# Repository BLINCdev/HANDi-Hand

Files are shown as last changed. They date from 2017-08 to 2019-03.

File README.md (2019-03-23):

__HITEC HS 35-HD DISCONTINUATION NOTICE:__ The Hitec servos used in this design have unfortunately been discontinued. We are currently testing other servo options. If you have built or would like to build a HANDi Hand, and would like information about pre-release parts for the new servo change design, please reach out to us at blincdev@gmail.com.

# HANDi Hand
The Humanoid, Anthropometric, Naturally Dexterous, Intelligent (HANDi) Hand is an anthropometric robotic hand designed specifically for machine learning research in prosthetic applications. The HANDi Hand includes 6 degrees of freedom (each finger flexes independently; thumb rotation is separate from thumb flexion). The hand was designed to be 1:1 scale with anatomical proportions and uses Hitec HS-35HD servo-motors. The HANDi Hand is ideally suited for machine learning and sensory feedback research, but can also be used in general purpose robotics applications.

## Build your own HANDi Hand
The HANDi Hand consists of off-the-shelf servomotors, potentiometers, FSRs, metric fasteners, and custom 3D printed parts. Instructions for building the hand and setting up the servos can be found in _'HANDi Hand - Assembly Manual.pdf'_. The assembly manual will be your main go-to document while printing and building the arm and includes references to the other files in the repository:

* __3D Print Files:__ The folder that contains the raw STL files as well as the .THING and .x3g files for 3D printing on a Makerbot Replicator 2. NOTE: The STL files have been adjusted to print with proper tolerances in the PLA material. Further, the print orientation is important for many of the files; refer to the .thing files provided if printing .STL files with other softwares besides MakerWare to ensure the proper print orientation.
* __STEP Files:__ This folder contains the STEP files for each of the parts used in the hand, which should be importable into most 3D CAD softwares.
* __Software:__ This folder contains Arduino sketches that are used for testing the hand during assembly, as well as control of the hand once assembly is complete.

The assembly manual also includes a Bill of Materials: a detailed list of the off-the-shelf materials and parts required to build the HANDi Hand. Note: We have listed the distributors that we have used in the past as a point of reference, but be aware that there are multiple distributor options for each part and that we do not endorse the listed distributors in any way.

## Contributing
You can share your experience, new design, ideas, feature requests, or questions on the [HANDi Hand project forum](https://blincdev.ca/forum/).

If you would like to contribute to future official releases of the HANDi Hand hardware we recommend contacting us on the forums to coordinate with our development team. To get started you will need to [fork this repo](https://help.github.com/articles/using-pull-requests/) and once your modification or enhancement is complete submit a [pull request](https://help.github.com/articles/using-pull-requests/).

## License
The HANDi Hand hardware is released under the [Creative Commons BY-SA 4.0](http://creativecommons.org/licenses/by-sa/4.0/) license. A local copy of the license that was forked from [https://github.com/idleberg/Creative-Commons-4.0-Markdown](https://github.com/idleberg/Creative-Commons-4.0-Markdown) is available in the repository. The HANDi Hand software is released under the [GNU General Public License v3](https://www.gnu.org/licenses/gpl.html). A local copy is available in the repository.

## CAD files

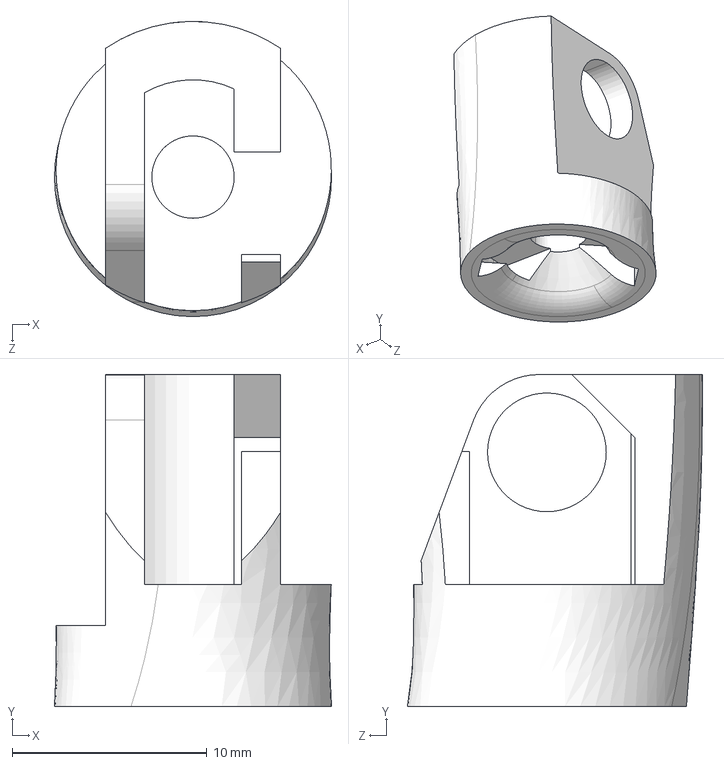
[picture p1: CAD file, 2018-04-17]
Hardware/Left Hand/STEP Files/DP - P Main L.STEP
14.2 x 17.1 x 15.2 mm

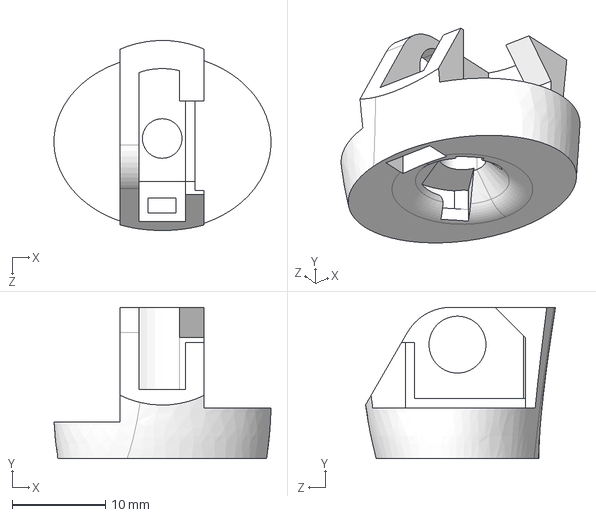
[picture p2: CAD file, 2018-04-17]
Hardware/Right Hand/STEP Files/DP - P MainTH R.STEP
23.2 x 16.2 x 20.4 mm

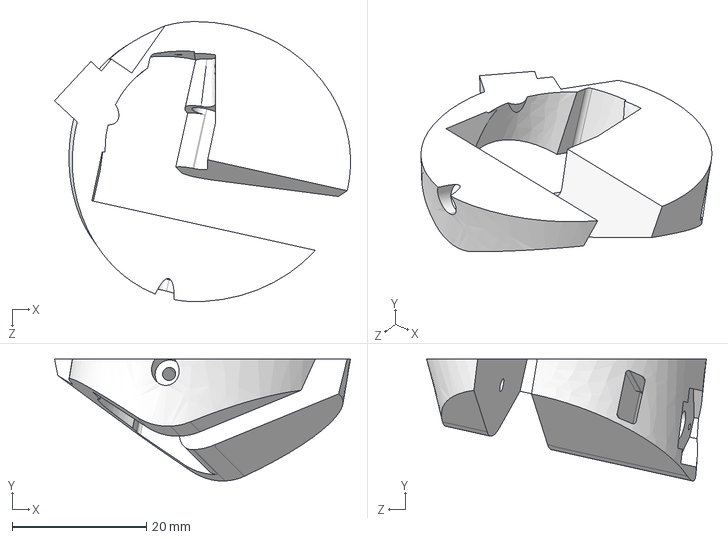
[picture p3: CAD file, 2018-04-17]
Hardware/Right Hand/STEP Files/MC - P Main R - Add B.STEP
44.2 x 18.2 x 41.8 mm

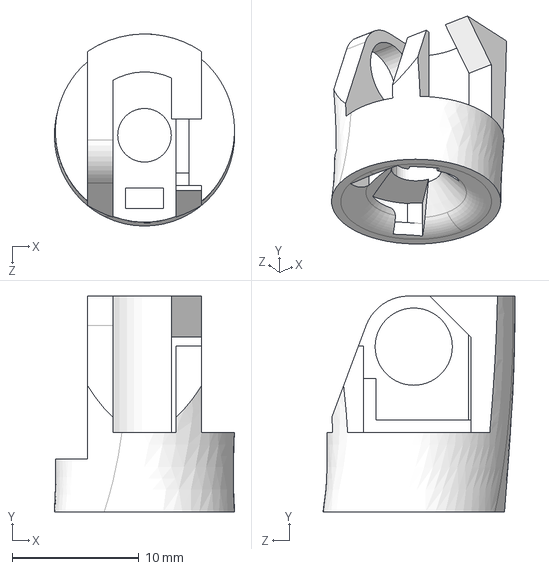
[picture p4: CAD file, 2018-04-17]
Hardware/Right Hand/STEP Files/DP - P Main R.STEP
14.2 x 17.1 x 15.2 mm

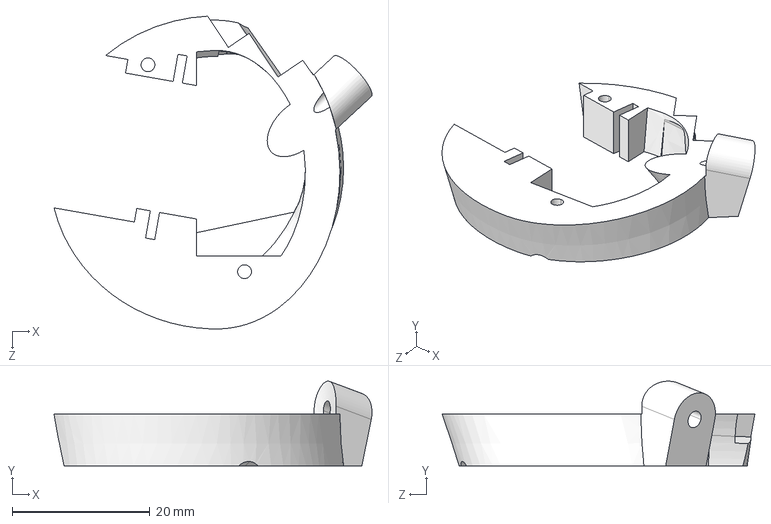
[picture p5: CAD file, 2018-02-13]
Hardware/Left Hand/STEP Files/MC - P Main L - Add A.step
46.1 x 12.3 x 45.3 mm

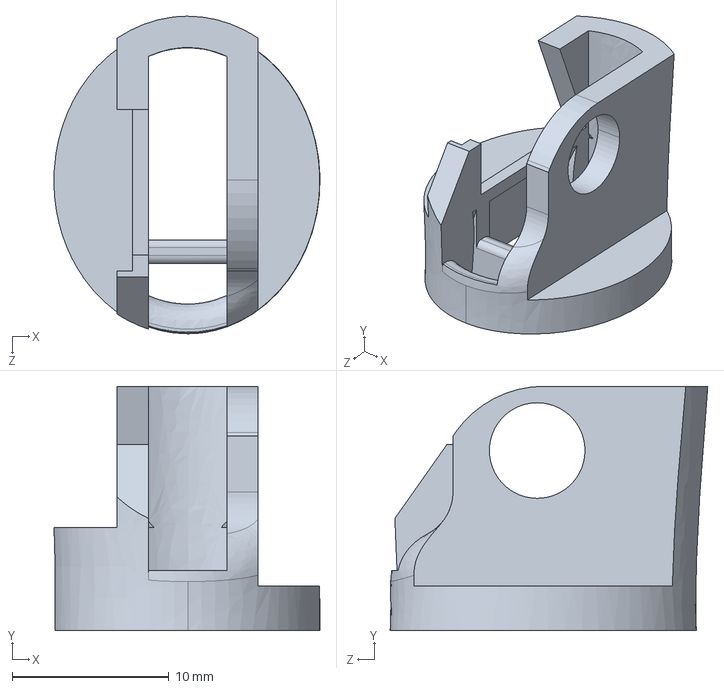
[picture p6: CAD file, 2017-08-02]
Hardware/Left Hand/STEP Files/PP - P MainD2 L.STEP
17.0 x 15.6 x 20.3 mm

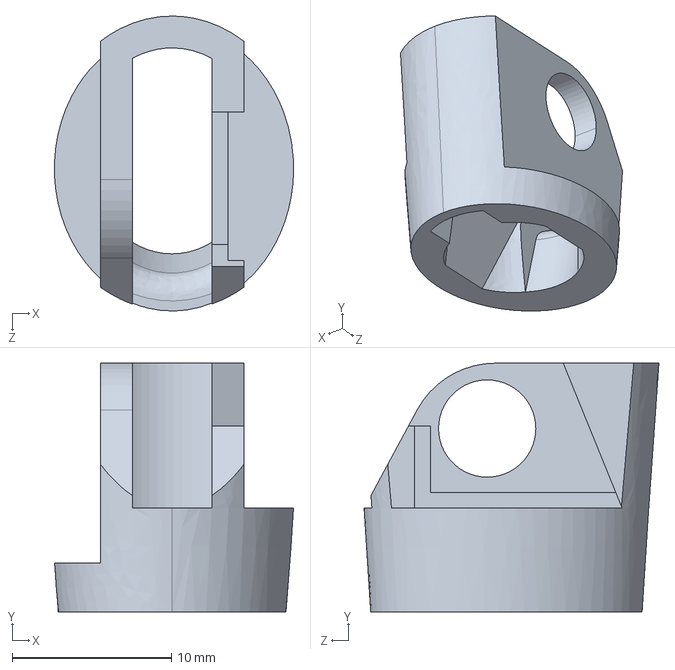
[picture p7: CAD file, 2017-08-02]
Hardware/Right Hand/STEP Files/IP - P Main R.STEP
15.0 x 15.6 x 18.5 mm

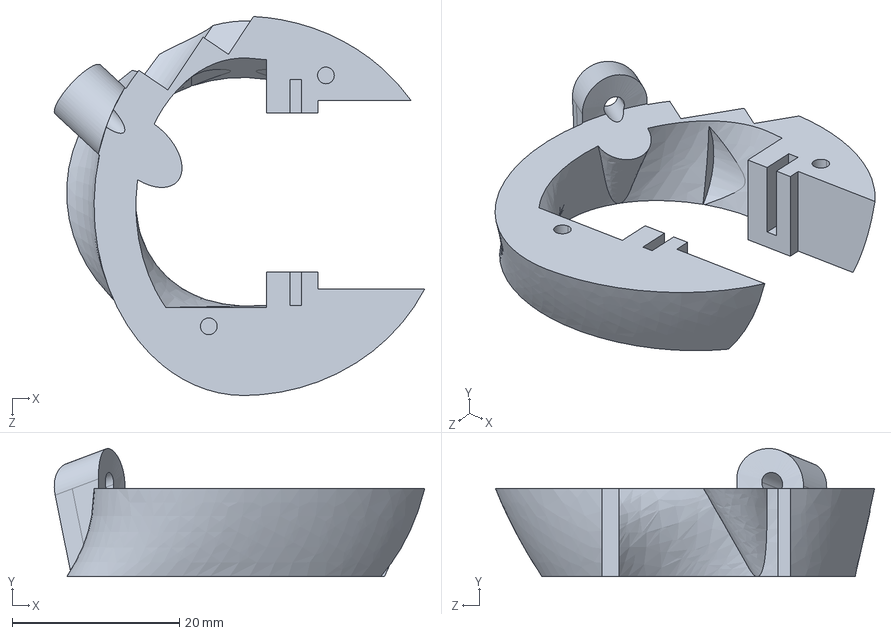
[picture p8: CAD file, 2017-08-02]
Hardware/Right Hand/STEP Files/MC - P Main R.STEP
44.3 x 15.3 x 45.3 mm

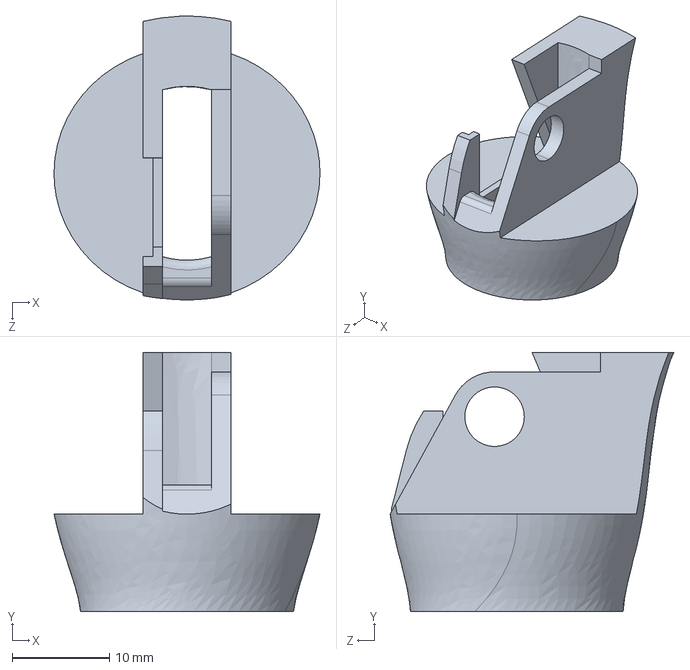
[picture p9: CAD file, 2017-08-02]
Hardware/Left Hand/STEP Files/IP - P MainTH L.STEP
27.3 x 26.6 x 29.1 mm

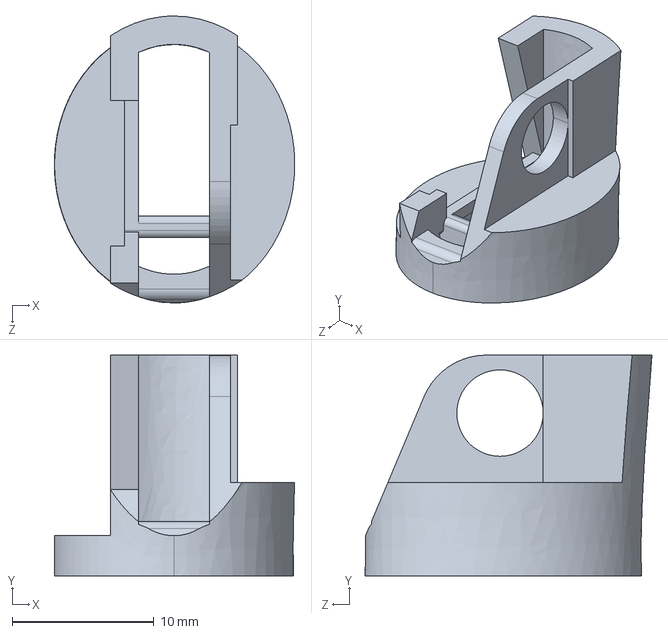
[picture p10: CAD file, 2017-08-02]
Hardware/Left Hand/STEP Files/PP - P MainD5 L.STEP
17.0 x 15.6 x 20.3 mm

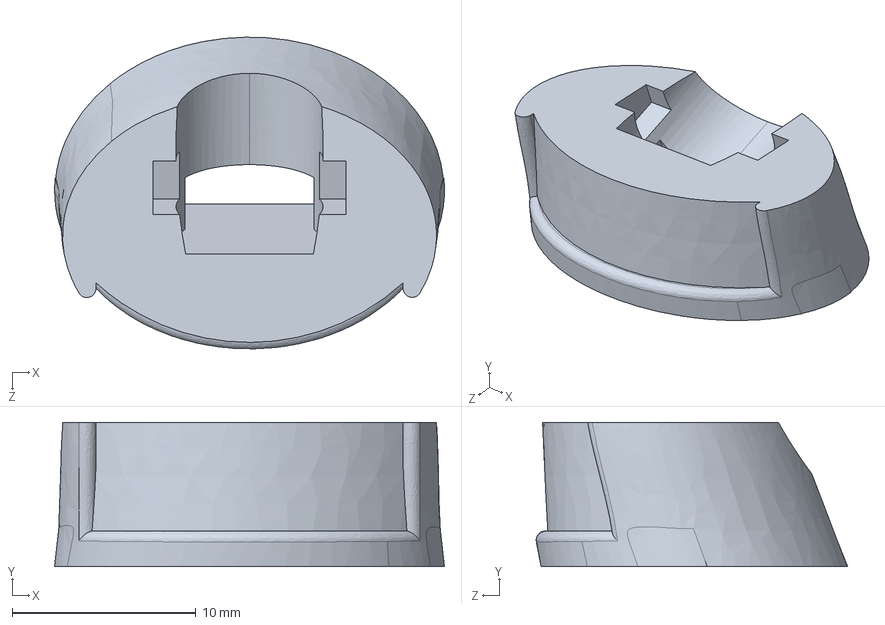
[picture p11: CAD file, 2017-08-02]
Hardware/Right Hand/STEP Files/DP - D MainTH.STEP
21.2 x 7.85 x 16.9 mm

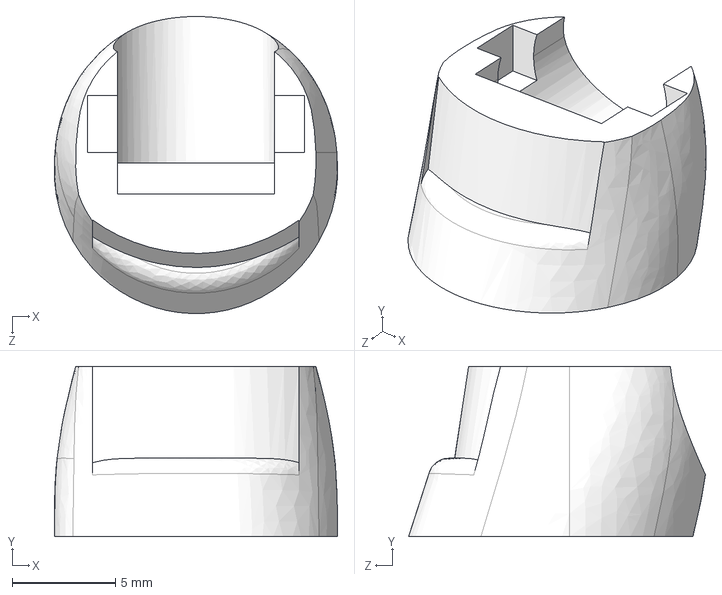
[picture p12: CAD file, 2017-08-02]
Hardware/Right Hand/STEP Files/DP - D Main.STEP
13.7 x 8.25 x 14.4 mm

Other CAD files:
Hardware/Left Hand/STEP Files/DP - P MainTH L.STEP
Hardware/Left Hand/STEP Files/MC - P Main L - Add B.step
Hardware/Right Hand/STEP Files/MC - P Main R - Add A.STEP
Hardware/Left Hand/STEP Files/IP - P Main L.STEP
Hardware/Right Hand/STEP Files/IP - P MainTH R.STEP
Hardware/Left Hand/STEP Files/PP - P MainD4 L.STEP
Hardware/Left Hand/3d Print Files/STL Files/Breadboard.STL
Hardware/Left Hand/3d Print Files/STL Files/Connector Hub.STL
Hardware/Left Hand/3d Print Files/STL Files/DP - D FSR Actuator.STL
Hardware/Left Hand/3d Print Files/STL Files/DP - D FSR ActuatorTH.STL
Hardware/Left Hand/3d Print Files/STL Files/DP - D Lock.STL
Hardware/Left Hand/3d Print Files/STL Files/DP - D LockTH.STL
Hardware/Left Hand/3d Print Files/STL Files/DP - D Main.STL
Hardware/Left Hand/3d Print Files/STL Files/DP - D MainTH.STL
Hardware/Left Hand/3d Print Files/STL Files/DP - D Tip.STL
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

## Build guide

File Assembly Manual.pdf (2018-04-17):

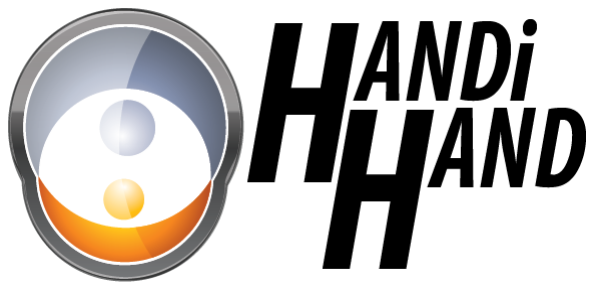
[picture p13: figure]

# Assembly Manual

Dylan Brenneis

July 2017

James Austin

Updated December 2017

i

## Contents

Table of Figures | ii
1 | Introduction | 2
2 | Naming and Definitions | 3
2.1 Digits | 3
2.2 Joints | 3
2.3 Finger Parts | 3
3 Required Materials | 4
3.1 3D Printed Parts | 4
3.2 Ordered Parts | 5
3.3 Tools | 7
4 | Assembly Flowchart | 7
5 | Material Preparation | 8
5.1 3D Printed Parts (17h 0m) | 8
5.2 Potentiometers (1h 45m) | 9
5.3 FSRs (1h 0m) | 10
5.3.1 Fingertips | 11
5.4 Screws (0h 45m) | 11
6 Thumb Assembly (1h 0m) | 12
6.1 Part Assembly | 12
6.2 Optional: Add.able Thumb Assembly | 13
6.3 Mounting to Palm | 15
7 | Finger Assembly (0h 15m each finger) | 15
8 | Servo Installation and Finger Tensioning (0h 7m each finger) | 16
9 | Breadboard Hub (3h 0m) | 18
10 | Aluminum Servo Cover (0h 45m) | 21
11 | Ventral Palm Cover; USB Webcam (0h 20m) | 21
12 | Palm Grips (1h 15m) | 22
13 | Wiring (1h 0m) | 23
13.1 Testing | 23
13.2 Full Implementation | 24
14 | Appendix A: Grip Pattern Template | I
15 | Appendix B: Servo Cover Template | 3

ii

## Table of Figures

Figure 1: Digit numbering | 3
Figure 2: Joint names | 3
Figure 3: Example part naming convention | 3
Figure 4: Dorsal Palm post processing | 9
Figure 5: Sanding locations for finger joints | 9
Figure 6: Filing of DP - D Lock | 9
Figure 7: Potentiometer polarity | 10
Figure 8: Finished potentiometers | 10
Figure 9: Fingertip assembly diagram | 11
Figure 10: Finished fingertip without grip pads | 11
Figure 11: Thumb assembly diagram | 12
Figure 12: Assembled thumb prior to MC - P Geared Rotator installation, showing servo position .........12
Figure 13: Add.able thumb assembly diagram | 14
Figure 14: Thumb mounted to dorsal palm | 15
Figure 15: Index finger (D2) assembly diagram | 15
Figure 17: Zip-tie receiver installed in servo spool (left), and zip-tie installed in thumb servo spool (right)
| 16
Figure 16: Full Forward Position of servo | 16
Figure 18: Servo spool installation on servo | 17
Figure 19: Required cut for zip-tie | 17
Figure 20: Servo installation and finger tensioning complete, showing servo positions for right and left
hand | 17
Figure 21: Breadboard clips salvaged from mini breadboard, cut and soldered as necessary | 18
Figure 22: Prototyping wire soldered to individual breadboard clip | 18
Figure 23: Soldered connections | 18
Figure 24: Molex connector configurations | 19
Figure 25: Breadboard orientation on hub | 19
Figure 26: Finished soldered connections for breadboard hub, top and front view | 19
Figure 27: Finished breadboard hub | 20
Figure 28: Pinout for breadboard hub. Breadboard holes to the left of the green line correspond to sensor signal connections; holes to the right correspond to servo motor command signals. Use this diagram as a
reference when connecting the wiring to ensure proper connection | 20
Figure 29: Installation of aluminum servo covers (left hand) | 21
Figure 30: USB Webcam installed in ventral palm (right hand) | 21
Figure 31: Grip diagram | 22
Figure 32: Test Setup Wiring | 23
Figure 33: Full wiring diagram for individual finger potentiometer control | 24
Figure 34: Full wiring diagram | 25

## 1 Introduction

The HANDi Hand was designed as an open-source robotic platform specifically designed for machine learning research. The inexpensive and easily modifiable design allows versatility for research studies, and the suite of sensors provides valuable information for machine learning and prosthetics research.

The open-source release provides all solid-modelling files, .stl files, Arduino code, and assembly instruction required to construct a fully functional HANDi Hand, and should also give the maker enough flexibility to make alterations to the design as necessary to suit their own needs. Both left and right hand versions are available. To contact the original designers, or to receive support for your build, please visit BLINCdev.ca.

This assembly manual outlines all the information required to print and source parts, and assemble the HANDi Hand as currently designed. The hand takes an estimated 30 hours to build.

## 2 Naming and Definitions

This section outlines the naming conventions for the various parts of the hand.

### 2.1 Digits

The digits are referred to by standard numbering, beginning with the
thumb as D1 (See Figure 1).

### 2.2 Joints

The joints are named in accordance with Figure 2. The names are constructed first with a digit indicator (i.e. D2) followed by a joint indicator D, I or P, indicating distal, intermediate, or proximal respectively. Potentiometers are named for the joints that they measure. The digit D0 refers to thumb rotation. The digit D1A refers to thumb adduction if implementing the Add.able Thumb option.

### 2.3 Finger Parts

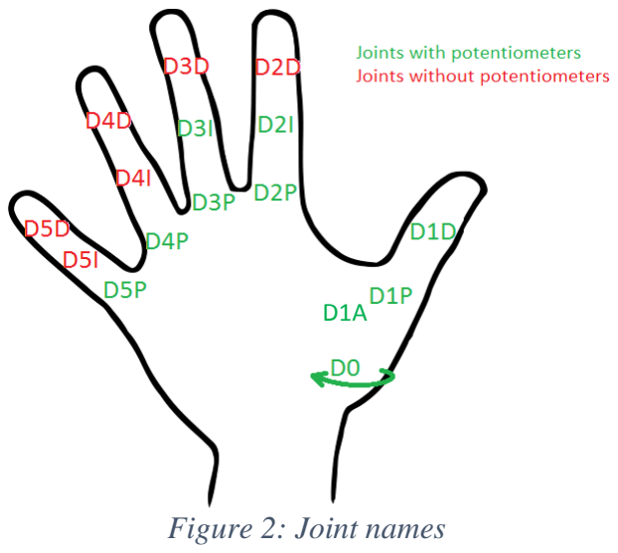
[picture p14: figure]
Figure 2: Joint names

Each phalanx of the finger is made up of multiple parts. The parts are named with convention in Figure 3:

1: Phalanx indicator. PP = Proximal Phalanx, IP = Intermediate Phalanx, DP = Distal Phalanx, MC = Metacarpal

2: Part position indicator. P = Proximal, D = Distal

Figure 3: Example part naming convention

3: Position modifier. There are sometimes multiple parts in the same location that must be differentiated by their function (pivot, main, lock, tip, etc).

4: Handedness indicator. R = Right Hand, L = Left Hand

## 3 Required Materials

### 3.1 3D Printed Parts

The 3D printed parts are designed to be printed in PLA without support material and without rafts, except where indicated. Parts are designed for the print tolerance of a MakerBot Replicator 2. Some filing may be necessary to ensure a smooth running fit between parts.

All files required for 3D printing can be accessed via BLINCdev.ca. The suggested print specifications for each part are found in Table 1. The table lists all of the part sets that must be printed for a complete hand. In the event that a particular component is needed, the individual STL files can be found on blincdev.ca in addition to the grouped parts in Table 1.

To determine whether to print “Full Thumb” or “Full Add Thumb”, see Section 6.2

Table 1: 3D printed parts

Part Name | Print Specifications | Estimated Print Time | Est. Material Weight
Dorsal Palm | 0.2 mm layer, 10% infill Print with raft | 6h 0m | 64 g
Ventral Palm | 0.2 mm layer, 10% infill | 1h 55m | 22 g
Thumb Screw Cap | 0.2 mm layer, 10% infill | 0h 15m | 2 g
D2 Full Finger | 0.2 mm layer, 10% infill | 1h 10m | 9 g
D3 Full Finger | 0.2 mm layer, 10% infill | 1h 10m | 9 g
D4 Full Finger | 0.2 mm layer, 10% infill | 1h 10m | 9 g
D5 Full Finger | 0.2 mm layer, 10% infill | 1h 10m | 9 g
Full Thumb | 0.2 mm layer, 10% infill | 2h 30m | 25 g
Full Add Thumb | 0.2 mm layer, 10% infill | 3h 00m | 33 g
Breadboard | 0.1 mm layer, 10% infill | 0h 25m | 3 g
Connector Hub | 0.2 mm layer, 10% infill | 0h 15m | 3 g
Pot Activator Set of 15 | 0.1 mm layer, 10% infill | 0h 10m | 1 g
Pot Placeholder Set of 6 | 0.2 mm layer, 10% infill | 0h 10m | 2 g
Servo Spool Full Set | 0.1 mm layer, 10% infill | 0h 25m | 4 g
Servo Spur Gear | 0.1 mm layer, 10% infill | 0h 5m | 1 g
| TOTAL: | 16h 50m | 163 g

### 3.2 Ordered Parts

The table below contains all the items (excluding tools) required for building a complete HANDi Hand.

Table 2: Parts for ordering

Item | Description | Vendor | Part No. | Link | QTY | Cost/ Item
Ext. Cost | Curr. | Notes

SENSORS/ELECTRONICS
Sensor Rotary Position SMD | Rotary Position Sensor, muRata Electronics | Digi-Key | 490-14859-1-ND (Digi-Key) SV03A103AEA01R 00 (MFG) | https://www.digikey.ca/product-detail/en/murata-electronics-north-america/SV03A103AEA01R00/490-14859-1-ND/6623608 | 9* | $1.71 | $15.39 | CAD | Quantity is 10 if implementing the Add.able Thumb option.
400 Short Tail with solder tabs | FSR 400 (force sensitive resistor) with short tail and solder tabs | Digi-Key | 1027-1014-ND (Digi-Key) 34-00004 (MFG) | https://www.digikey.ca/product-detail/en/interlink-electronics/34-00004/1027-1014-ND/2798665 | 5 | $15.46 | $77.30 | CAD
Arduino Mega | Board MCU MEGA2560 | Digi-Key | 1050-1018-ND | https://www.digikey.ca/pro duct-detail/en/A000067/1050-1018-ND/2639006 | 1 | $50.38 | $50.38 | CAD
Wall Adapter | AC/DC Wall Mount Adapter 5V 18W | Digi-Key | Q976-ND (Digi-Key) QAWA-18-5-US01 (MFG) | https://www.digikey.ca/pro duct-detail/en/qualtek/QAWA-18-5-US01/Q976-ND/6412294 | 2 | $21.14 | $42.28 | CAD
100 kOhm Resistor | RES 100K Ohm 1/4 Watt, 5% Axial | Digi-Key | 10KEBK-ND (Digi-Key) CFR16J100K (MFG) | https://www.digikey.ca/product-detail/en/1623927-1/A105979CT-ND/3477574 | 5 | $0.15 | $0.75 | CAD
DC Barrel Jack Adapter -Female | Barrel Jack adapter | Sparkfun | PRT-10288 | https://www.sparkfun.com/products/10288 | 1 | $2.95 | $2.95 | USD
Break Away Headers -Straight | Conn Header .100” SNGL STR 40 POS | Digi-Key | S1011EC-40-ND (Digi-Key) PRPC040SAAN-RC (MFG) | https://www.digikey.ca/products/en?keywords=S1011 EC-40-ND | 2 | $1.04 | $2.08 | CAN
Breadboard | Miniature Breadboard | Sparkfun | PRT-12043 | https://www.sparkfun.com/products/12043 | 1 | $3.95 | $3.95 | USD | Only the metal connectors are required for assembly; any breadboard will do. See Section 9
Molex Receptacle Housing | 4POS 2MM Sherlock | Digi-Key | WM5983-ND (Digi-Key) 0355070400 (MFG) | https://www.digikey.ca/products/en?keywords=WM5 983-ND | 2 | $0.24 | $0.48 | CAN
Molex Receptacle Housing | 6POS 2MM Sherlock | Digi-Key | WM5985-ND (Digi-Key) 0355070600 (MFG) | https://www.digikey.ca/products/en?keywords=WM5 985-ND | 2 | $0.28 | $0.56 | CAN

Molex Header | 4POS 2MM Vert Tin Sherlock | Digi-Key | WM18922-ND (Digi-Key) 3562-0450 (MFG) | https://www.digikey.ca/products/en?keywords=WM1 8922-ND | 2 | $0.47 | $0.94 | CAN
Molex Header | 6POS 2MM Vert Tin Sherlock | Digi-Key | WM18924-ND (Digi-Key) 0353620650 (MFG) | https://www.digikey.ca/products/en?keywords=WM1 8924-ND%20 | 2 | $0.61 | $1.22 | CAN
Terminal contact | CONN TERM FEMALE 24-30 AWG TIN | Digi-Key | WM6050-ND (Digi-Key) 0502128100 (MFG) | https://www.digikey.ca/products/en?vendor=0&keywords=50212-8100 | 20 | $0.375 | $7.50 | CAD
Molex Receptacle Housing | Mini SPOX 2POS 2.5MM SHROUD | Digi-Key | WM18873-ND (Digi-Key) 0050375023 (MFG) | https://www.digikey.ca/products/en?vendor=0&keywords=50375023 | 2 | $0.30 | $0.60 | CAD
Molex Header | Mini SPOX 2POS 2.5MM Vert Tin | Digi-Key | WM18886-ND (Digi-Key) 0022035025 (MFG) | https://www.digikey.ca/products/en?vendor=0&keywords=22035025 | 2 | $0.68 | $1.36 | CAD
Terminal contact | CONN TERM FEMALE 22-28 AWG CRIMP | Digi-Key | WM17406-ND (Digi-Key) 0008701040 | https://www.digikey.ca/products/en?x=0&y=0&lang=en&site=ca&KeyWords=0 8701040 | 4 | $0.33 | $1.32 | CAD
Heat Shrink Tubing | Assorted Heat Shrink Tubing | Sparkfun | PRT-09353 | https://www.sparkfun.com/products/9353 | 1 | $7.95 | $7.95 | USD | Red, black, and yellow 1.5mm diameter required for assembly, approximately 2-3 pieces of each
Logitech Quick-Cam Pro | Clip-on USB Webcam | Amazon | N/A | https://www.amazon.ca/Lo gitech-QuickCam-Pro-for-Notebooks/dp/B000RZNI4 S | 1 | $203.16 | $203.16 | CAD | *See note below.
Hitec HS 35HD Servo | Ultra-Nano Analog servo, 180 degree rotation | Sparkfun | ROB-11882 | https://www.sparkfun.com/products/11882 | 6 | $24.95 | $149.70 | USD

MATERIALS
Medium-Strength Textured Neoprene Rubber | Adhesive Back, 1/32" thick, 12"x12", 40A Durometer Hardness | McMaster-Carr | 8445K61 | https://www.mcmaster.com/#8445k61/=18l0h88 | 1 | $11.08 | $11.08 | USD | Approximately 2000 mm^2 needed for assembly
Easy-to-Weld Corrosion-Resistant 5052 Aluminum | Sheet, 0.080" Thick, 6" x 6" | McMaster-Carr | 88895K105 | https://www.mcmaster.com/#88895k105/=18l0irl | 1 | $5.78 | $5.78 | USD

HARDWARE/MISCELLANEOUS

Continuous -Flex Wire | 26-gauge continuous flex wire, 50', Black | McMaster-Carr | 7071K19 | https://www.mcmaster.com/#7071k19/=18l0k9k | 50 | $1.20 | $60.00 | USD | Approximately 50' needed for in-hand wiring, 50' for hand-arm wiring
Metric Cheese Head Slotted Machine Screw | 18-8 Stainless Steel, M2 Size, 25 mm Length, .4mm Pitch, Pack of 50 | McMaster-Carr | 91800A023 | https://www.mcmaster.com/#91800a023/=18l0ku6 | 1 | $7.45 | $7.45 | USD | 16 needed for assembly, 14 of which are cut to size as in Section 5.4 2 additional cut screws needed if implementing the Add.able Thumb option.
Loctite Instant-Bonding Adhesive | #404, 0.3 oz Bottle | McMaster-Carr | 7569A22 | https://www.mcmaster.com/#7569a22/=18l0vy5 | 1 | $27.37 | $27.37 | USD | Any super-glue will work.
Type 18-8 Stainless Steel Flat Washer | M2.5 Screw Size, 2.2mm ID, 5.0mm OD, Pack of 100 | McMaster-Carr | 93475A195 | https://www.mcmaster.com/?error_redirect=true%20 -%2093475a196/=x3cpi7#9 3475a195/=18l0xfy | 1 | $1.06 | $1.06 | USD | 16 needed for assembly
Cable Tie | CBL TIE Locking NAT 18LB 5.9” | Digi-Key | Q731-ND (Digi-Key) 17-M150N-C | https://www.digikey.ca/products/en?keywords=Q731-ND | 100 | $0.084 | $8.40 | CAD | 9 needed for assembly
TOTAL: | | | | | | | $760.33 | CAD | Delivery costs not included. Currency conversion of 1 CAD = 0.80 USD

* This is the camera the hand is currently designed for. Cheaper cameras could work just as well with a little re-designing of the mounts on the ventral palm.

### 3.3 Tools

The following tools are required to create a HANDi Hand:

- 3D printer (MakerBot Replicator 2
suggested)
- Dremel tool with sanding wheel
- 120 grit sandpaper
- Small files
- Narrow flat screwdriver
- #0 Philips screwdriver
- Tin snips
- Large flat metal file
- Wire strippers
- Soldering iron and solder
- Heat gun
- Hobby knife
- Fine tweezers
- Needlenose pliers
- Wire cutter

## 4 Assembly Flowchart

A particular order of operations must be followed when assembling the hand, and is outlined in the following flowchart. A process described in any bubble cannot be completed until all items attached to incoming arrows have been completed.

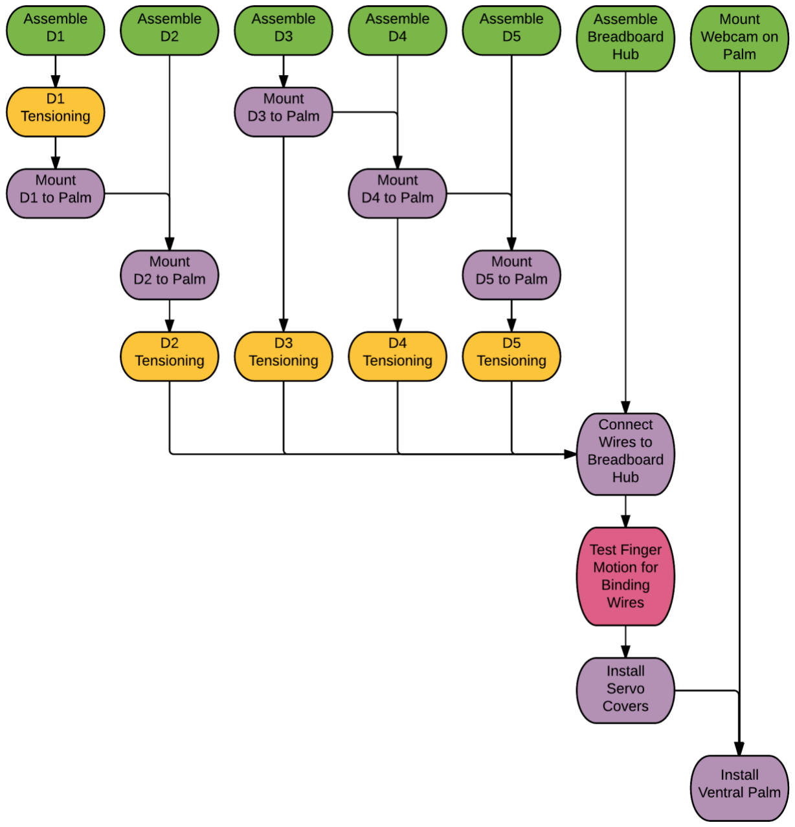
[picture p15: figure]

## 5 Material Preparation

### 5.1 3D Printed Parts (17h 0m)

Print parts as specified in section 3.1 The parts are designed to involve as little post-processing as possible; however a few things should be done.

1. Dorsal Palm: Remove print supports using needlenose pliers, then sand smooth using dremel tool with sanding wheel. See Figure 4. The inside faces of the connections with the fingers should also be sanded using 120 grit sandpaper, to ensure a smooth running fit.

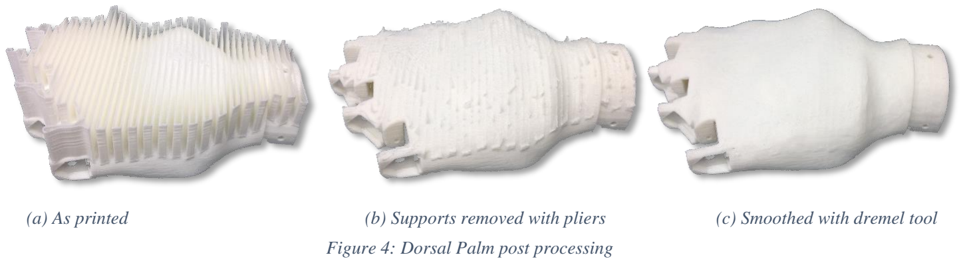
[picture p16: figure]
Figure 4: Dorsal Palm post processing

2. Finger Joints: The outside faces of all XP – P Main and XP – P Pivot parts, as well as the inside faces of all XP – D parts should be sanded lightly with 120 grit sandpaper to ensure a smooth running fit between the parts. Figure 5 shows the locations that need to be sanded for the intermediate joint of the fingers. Proximal and distal joints will also need to be sanded. It is best to install the pivot parts in the main parts prior to sanding. Any surfaces that will be glued should also be sanded; refer to Figure 11 and Figure 15.
3. Fingertip Locks: the locking wings on all DP – D Lock parts should be filed slightly using a small semi-rounded file. The goal is to have them twist into a locked position with the DP – P Main parts. They should therefore be filed such that the twisting motion is possible, but sufficient friction still exists to keep the fingertips in the locked position.

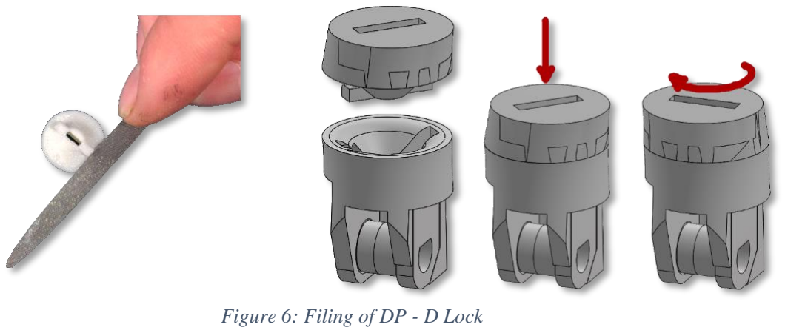
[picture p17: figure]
Figure 6: Filing of DP - D Lock

4. Breadboard and Connector Hub: the holes in these parts will likely be partially occluded by the 3D printed plastic. It is recommended that these holes be drilled out after printing using a .95 mm drill bit.

### 5.2 Potentiometers (1h 45m)

In the current version, there are 9 potentiometers (limited due to the number of analog input pins on the Arduino Mega); the Add.able Thumb options uses one additional potentiometer. The suggested lengths of the connecting wires are found in Table 3:

Figure 5: Sanding locations for finger joints

(a) As printed | (b) Supports removed with pliers | (c) Smoothed with dremel tool

Table 3: Suggested wire lengths for potentiometers

Potentiometer ID | Suggested Wire Length
D0 | 150 mm
D1A | 150 mm
D1P | 150 mm
D1D | 190 mm
D2P | 150 mm
D2I | 190 mm
D3P | 150 mm
D3I | 190 mm
D4P | 150 mm
D5P | 150 mm
1. Cut off the top lone pin on the potentiometer as short as possible.
2. Solder the wires to the potentiometer and a straight pin header to the other end of each wire. See note below about D0.
3. Use black heat-shrink on the connections near the potentiometer, and coloured heat shrink on the far connections corresponding to the polarity noted in Figure 7.
4. Heat shrink the 3 wires together near the loose end using a light coloured heat shrink tubing. Label the wires here with the potentiometer ID.

Note: the straight pin headers for the D0 potentiometer must be soldered to the wires after the potentiometer is installed in MC – Geared Rotator, and the wires routed through the narrow channel. Black heat-shrink tubing near the potentiometer will not fit in this channel, so it is omitted. Figure 8 shows finished D0 and D3I potentiometers.

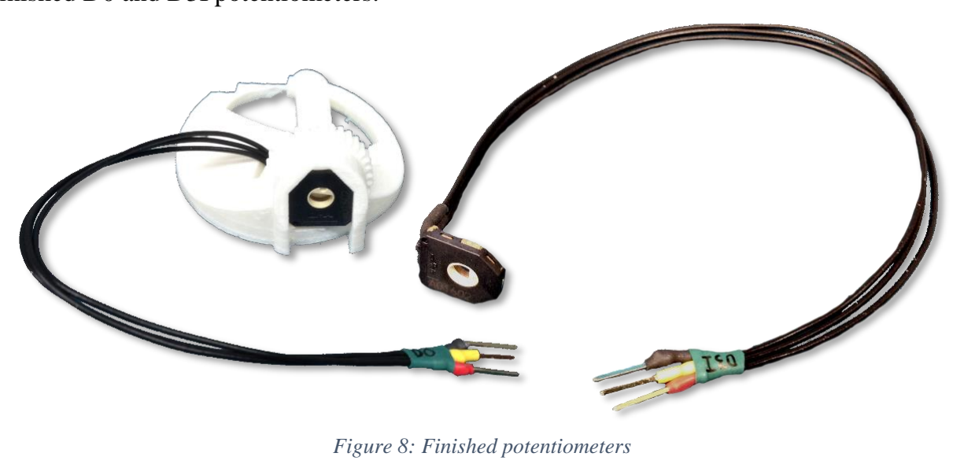
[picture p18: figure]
Figure 8: Finished potentiometers

### 5.3 FSRs (1h 0m)

Each fingertip requires an FSR. The recommended wire length for finger FSRs is 250 mm; for the thumb FSR 200 mm is recommended.

1. Solder each wire to the solder tabs of the FSR.
2. Install FSR in fingertip (see 5.3.1 ).
3. Use black heat-shrink tubing on the connections near the FSR.
4. Solder the wires to straight pin headers.

Figure 7: Potentiometer polarity

5. Use yellow and red heat shrink tubing on the connections with the straight pin headers.
6. Heat shrink the two wires together using a light coloured heat shrink, and label the wires here with the ID of the finger they represent.

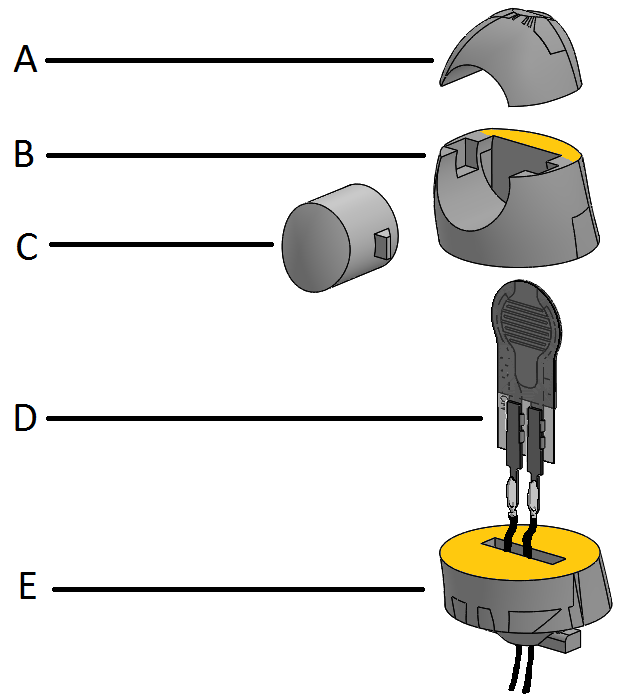
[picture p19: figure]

5.3.1 Fingertips
The fingertips should be assembled as per Figure 9. Use superglue on the surfaces marked in yellow. It is imperative that no glue should contact the FSR Actuator or the FSR itself; it should move freely inside the fingertip. The finished fingertip is shown in Figure 10.
A. DP – D Tip
B. DP – D Main
C. DP – D FSR Actuator
D. FSR400 Short Tail resistor
E. DP – D Lock

It is recommended that fingertip grip pads be cut from the neoprene rubber sheet (See section 12 ). Be careful when gluing the rubber to the fingertip that the movement of the FSR actuator does not become restricted in any way.

### 5.4 Screws (0h 45m)

The screws used as hinges in each of the finger joints are required to be cut to length from the 25 mm M2 screws. The lengths of the various screws can be referenced from Table 4. The screws should be cut to length in a manner such that the threads are preserved.

Table 4: Screw Lengths

Screw Position | Length of Screw Thread
D2D, D3D, D4D, D5D | 15 mm
D2I, D3I, D4I, D5I | 15.5 mm
D2P, D4P, D5P | 17.5 mm
D3P | 20.5 mm
D1D | 18.5 mm
D1P | 22 mm
D0 (both bottom and top screws) | 25 mm
Ventral Palm Screws (4) | 12 mm
Geared Rotator Screws (2) | 5 mm
D1A (both bottom and top screws) | 20.5 mm

Figure 9: Fingertip assembly diagram

Figure 10: Finished fingertip without grip pads

## 6 Thumb Assembly (1h 0m)

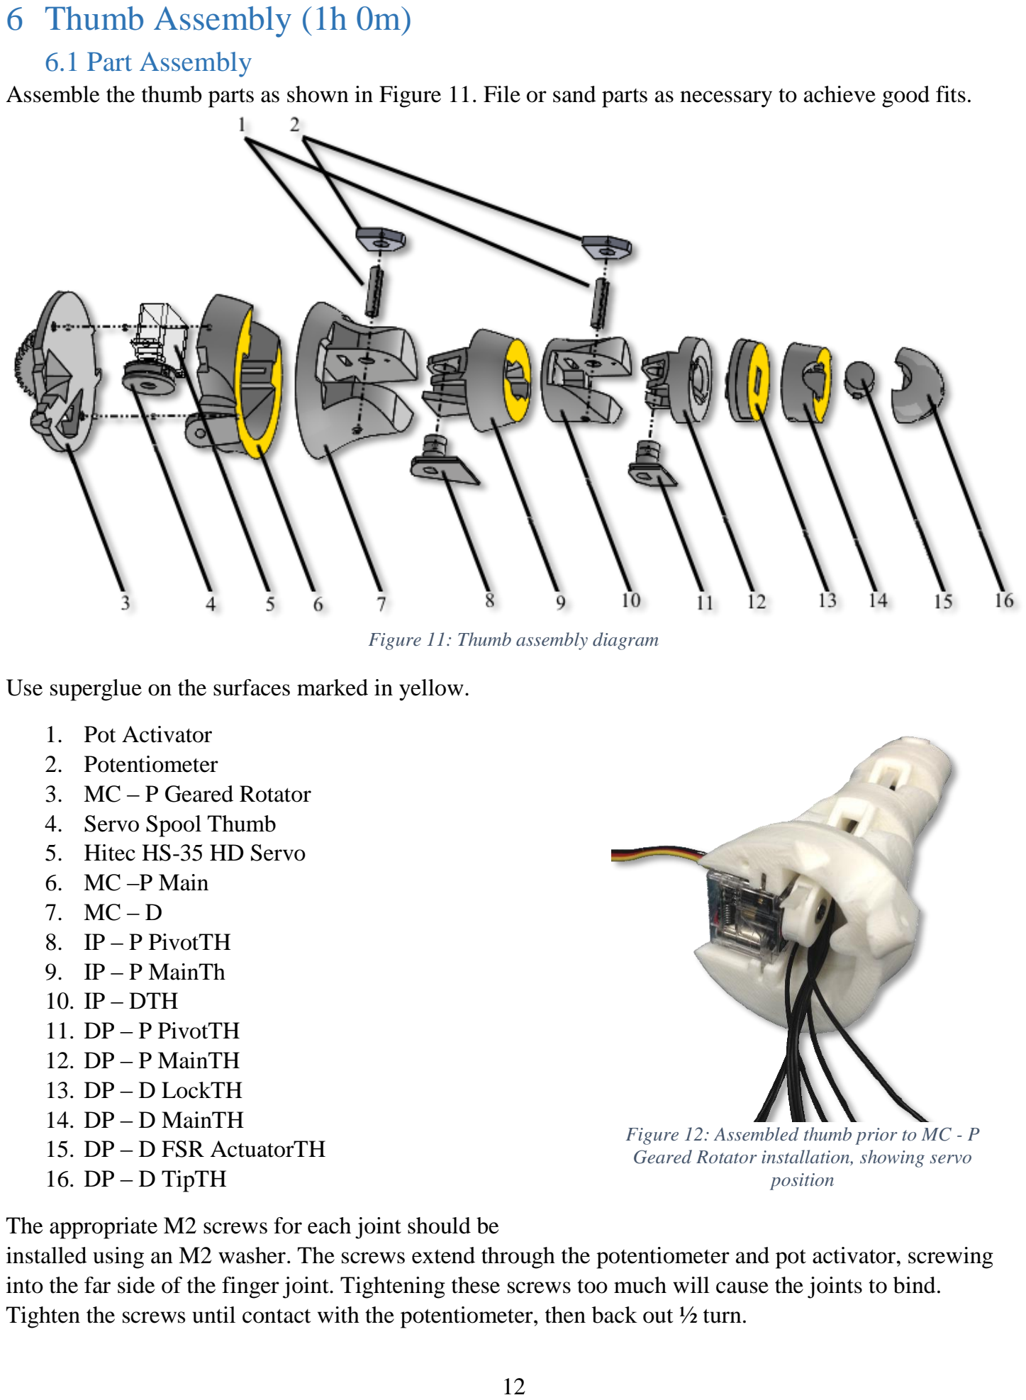
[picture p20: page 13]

### 6.1 Part Assembly

Assemble the thumb parts as shown in Figure 11. File or sand parts as necessary to achieve good fits.

Use superglue on the surfaces marked in yellow.

1. Pot Activator
2. Potentiometer
3. MC – P Geared Rotator
4. Servo Spool Thumb
5. Hitec HS-35 HD Servo
6. MC –P Main
7. MC – D
8. IP – P PivotTH
9. IP – P MainTh
10. IP – DTH
11. DP – P PivotTH
12. DP – P MainTH
13. DP – D LockTH
14. DP – D MainTH
15. DP – D FSR ActuatorTH
16. DP – D TipTH

The appropriate M2 screws for each joint should be
installed using an M2 washer. The screws extend through the potentiometer and pot activator, screwing into the far side of the finger joint. Tightening these screws too much will cause the joints to bind. Tighten the screws until contact with the potentiometer, then back out ½ turn.

Figure 11: Thumb assembly diagram

Figure 12: Assembled thumb prior to MC - P Geared Rotator installation, showing servo position

The thumb zip-tie should be installed and tensioned before the MC – P Geared Rotator is attached using two 5mm M2 screws. See Section 8 Figure 12 shows an assembled thumb prior to MC – P Geared Rotator installation, showing the correct servo positioning for full extension.

### 6.2 Optional: Add.able Thumb Assembly

The Add.able Thumb (short for “Adductable Thumb”) is an optional variant to the default HANDi Hand thumb assembly that adds an additional degree of freedom to the thumb digit, allowing it adduct (flex laterally towards the fingers) and abduct (extend laterally away from the fingers). Table 5 illustrates how the Add.able Thumb variant for the HANDi Hand compares with the default thumb assembly. To implement the Add.able Thumb instead of the default thumb, print the parts listed in this section instead of those listed in section 6.1; this can be done by printing the “Full Add Thumb” X3G file instead of the “Full Thumb” X3G file.

Table 5: Comparison of Default Thumb and Add.able Thumb Option

Property | Default Thumb | Add.able Thumb
Length from D0 Axis | 93 mm | 104 mm
Mass (printed parts only) | 27 grams | 33 grams
Degrees of Freedom | 2 | 3
Degrees of Actuation | 2 | 2
Grips Possible | Pinch Grip, Tripod Grip, Column Grip | Key Grip, Pinch Grip, Tripod Grip, Improved Column Grip

Note that if using an Arduino Mega, connecting to a potentiometer on the additional degree of freedom (D1A) will require replacing an existing connection pin, either by swapping an existing potentiometer out with a Pot Placeholder, or by giving up joystick control for an additional pin.

If implementing the Add.able Thumb option, assemble the thumb parts as shown in Figure 13. File or sand parts as necessary to achieve good fits. Note that the “Servo Spool Thumb – Add” part replaces the “Servo Spool Thumb” part used in the default thumb assembly.

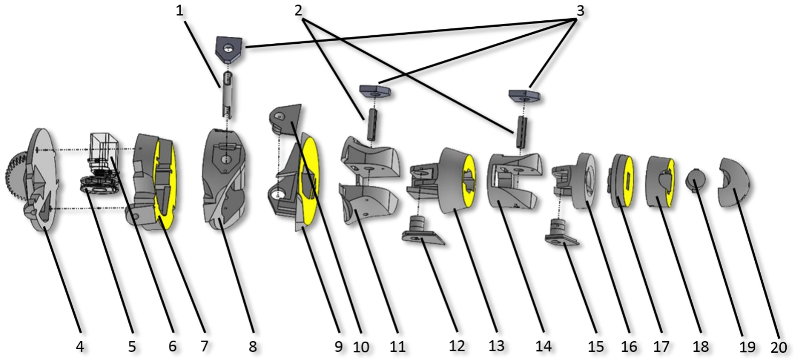
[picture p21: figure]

Figure 13: Add.able thumb assembly diagram

Use superglue on the surfaces marked in yellow.

1. Pot Activator – Add
2. Pot Activator
3. Potentiometer
4. MC – P Geared Rotator
5. Servo Spool Thumb – Add
6. Hitec HS-35 HD Servo
7. MC –P Main – Add A
8. MC –P Main – Add B
9. MC – D – Add A
10. MC – D – Add Pivot
11. MC – D – Add B
12. IP – P PivotTH
13. IP – P MainTh
14. IP – DTH
15. DP – P PivotTH
16. DP – P MainTH
17. DP – D LockTH
18. DP – D MainTH
19. DP – D FSR ActuatorTH
20. DP – D TipTH

Assemble and mount as per the standard thumb assembly and mounting instructions.

### 6.3 Mounting to Palm

Rotate the D0 servo with the small gear to the mounting position. Looking down from the top of the hand, this will be fully clockwise for a right hand assembly, and fully counter clockwise for a left hand assembly.

Position the thumb so that it is rotated outward as much as possible, and secure to the palm using two 25 mm M2 screws; one from the top and one from the bottom. Be sure to include a pot activator on the bottom side.

## 7 Finger Assembly (0h 15m each finger)

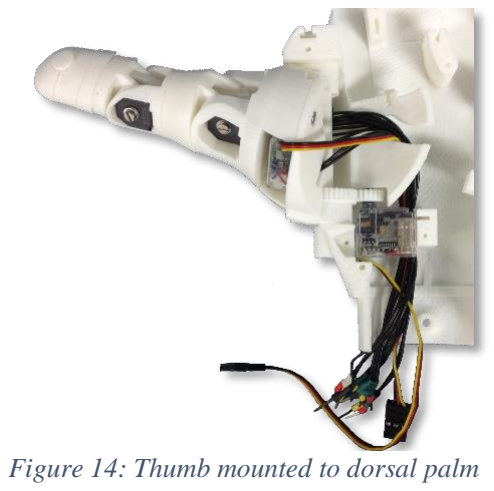
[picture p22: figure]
Figure 14: Thumb mounted to dorsal palm

Assemble the finger parts as shown in Figure 15. File or sand the parts as necessary to achieve good fits.

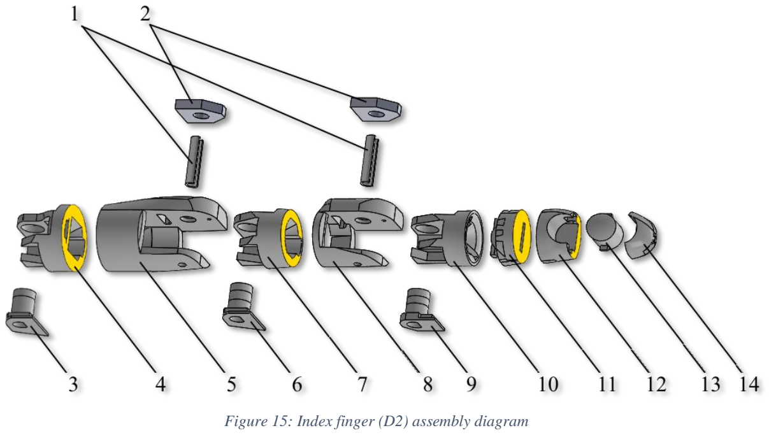
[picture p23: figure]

Use superglue on the faces marked in yellow.

1. Pot Activator
2. Potentiometer*
3. PP – P PivotD2**
4. PP – P MainD2**
5. PP – D
6. IP – P Pivot
7. IP – P Main
8. IP – P D
9. DP – P Pivot
10. DP – P Main
11. DP – D Lock
12. DP – D Main
13. DP – D FSR Actuator
14. DP – D Tip

* The number of potentiometers used, and their location depends on the finger. Wherever a potentiometer is omitted, a Pot Placeholder should be used in its place. For use with an Arduino

Figure 15: Index finger (D2) assembly diagram

Mega, the suggested potentiometer positions are given in Figure 2, Section 2.2 .A Pot Activator should be used regardless of whether a potentiometer or a Pot Placeholder is used.

** This assembly diagram shows the index finger (D2). For other fingers, substitute the appropriate parts here (i.e. D3 for middle finger, etc.).

## 8 Servo Installation and Finger Tensioning (0h 7m each finger)

Tensioning of fingers and thumb are identical processes, with the exception that the thumb servo spool will not include a zip-tie receiver. Here the tendon zip-tie passes directly through the spool.

1. Rotate servo to the full forward position using the Arduino sketch Pot_to_Servo_Control.ino. Wiring for this sketch is explained in section 13.1 . See Figure 16 for the definition of full forward position. Servo orientation matters for this operation, and changes depending on the finger in question. Refer to Figure 20 for correct servo positioning.

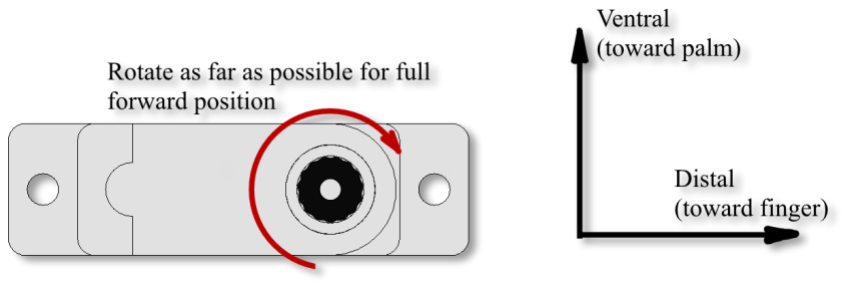
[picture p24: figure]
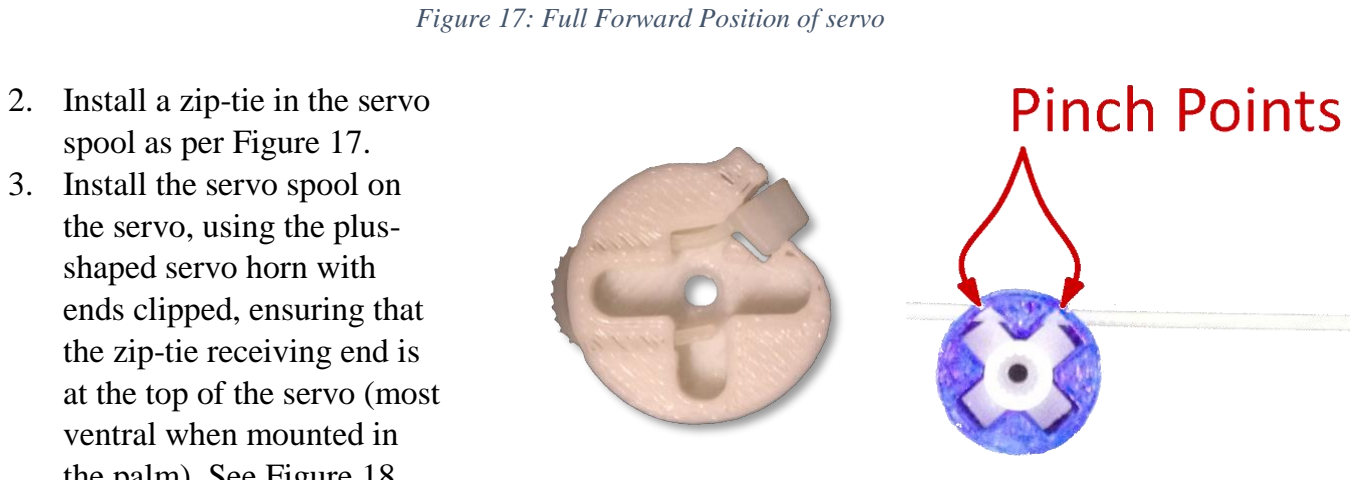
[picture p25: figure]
2. Install a zip-tie in the servo spool as per Figure 17. 3. Install the servo spool on the servo, using the plus- shaped servo horn with ends clipped, ensuring that the zip-tie receiving end is at the top of the servo (most ventral when mounted in

the palm). See Figure 18.
4. Cut a zip-tie’s receiving
end so that the thickness is
constant along the entire zip-tie. Sidecutters work best for this operation; fine adjustments can be made with a hobby knife when necessary. The cut is illustrated in Figure 19. This end of the zip-tie will serve as the stopper at the tip of the finger.

Figure 17: Full Forward Position of servo

Figure 16: Zip-tie receiver installed in servo spool (left), and zip-tie installed in thumb servo spool (right)

5. Thread the zip-tie through the finger from the distal to the proximal end, staying ventral to each of the joint pivots.
6. Pass the tendon zip-tie through the zip-tie receiver on the servo spool (or through the spool itself in the case of the thumb spool). There should be no slack in the zip-tie when the finger is fully extended, the servo is fully rotated forward, and the servo is installed in the dorsal palm. Trim the free end of the tendon zip-tie. Figure 20 shows the completed tensioning and servo installation.

Figure 18: Servo spool installation on servo

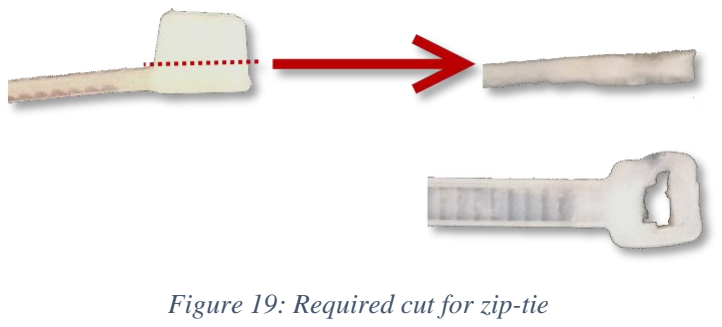
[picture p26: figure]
Figure 19: Required cut for zip-tie
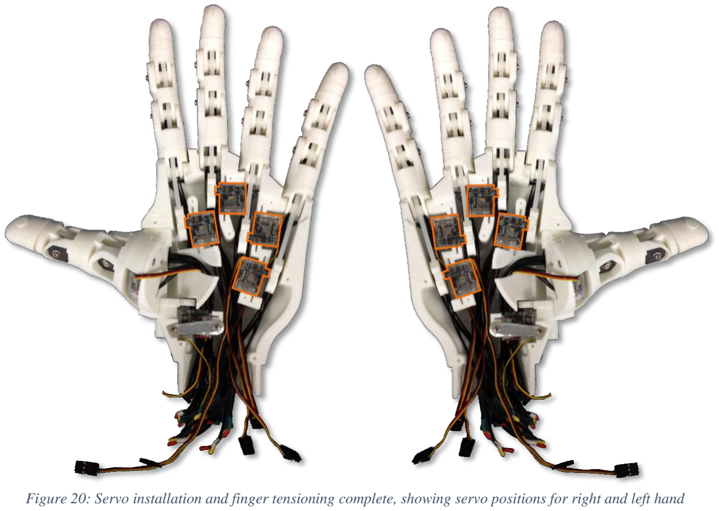
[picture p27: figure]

Figure 20: Servo installation and finger tensioning complete, showing servo positions for right and left hand

## 9 Breadboard Hub (3h 0m)

Creation of the breadboard hub is by far the most technically difficult and labor intensive operation in assembling the HANDi Hand, and is not required to have a fully functional hand. The breadboard hub reduces the number of wires leaving the hand from 60 to 22, which is important when interfacing with a movable arm since a large bulk of wires will tend to bind and restrict motion of the arm. Work is currently being done on the design of an in-palm PCB which will increase the sensing capabilities of the hand while simultaneously reducing the amount of wiring required. Please check BLINCdev.ca for information about upcoming releases.

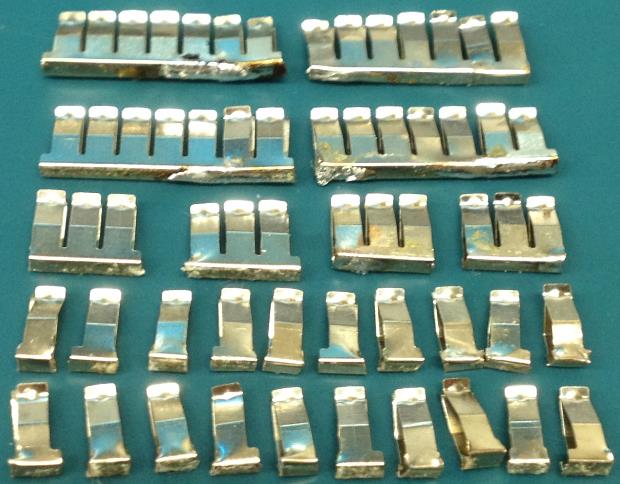
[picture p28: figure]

1. Print out the breadboard and connector hub with
the specifications given in Table 1, page 4.
Because it’s such a small part with finicky details, it sometimes won’t slice properly and can print with some of the insulating walls missing. If this is the case for you, glue some thin bits of plastic where the walls should be while you’re assembling the rest.
2. Remove the clips from the miniature breadboard, and cut/solder them together to obtain 4 clips with 7 receptacles, 4 with 3 receptacles, and 20 with 1 receptacle. When soldering the clips together for the 7 receptacle clips, be careful to
ensure that the receptacles line up with the holes
of the printed breadboard. Refer to Figure 21.
3. Solder a 1” piece of prototyping wire (22 AWG) to each single receptacle clip at the base (Figure 22).
4. Press-fit each of the receptacles into the bottom of the printed breadboard, making sure no part of any receptacle extends past the base of the board.
5. Solder jumper wires between the power
receptacles and ground receptacles as in Figure
23.
6. Test the board for proper conductivity at each receptacle. Adjust receptacle positioning if necessary.
7. Superglue the molex connectors to the connector hub, referring to Figure 24.
8. Superglue the printed breadboard to the other side of the connector hub, being careful to note the orientation shown in Figure 25.

Figure 21: Breadboard clips salvaged from mini breadboard, cut and soldered as necessary

Figure 22: Prototyping wire soldered to individual

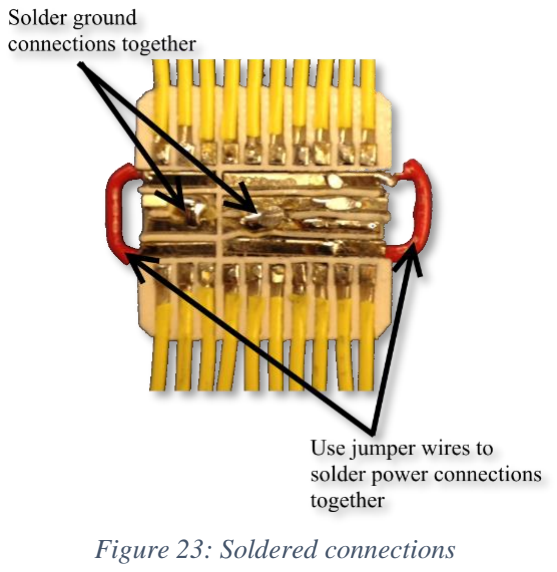
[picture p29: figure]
Figure 23: Soldered connections
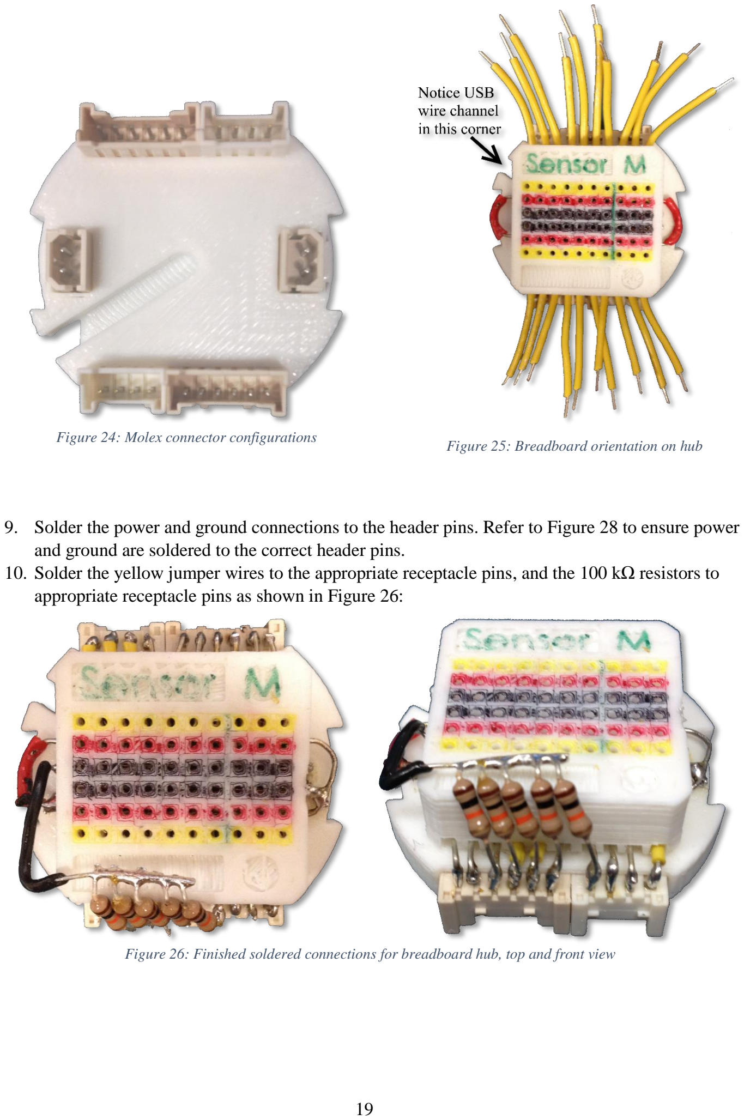
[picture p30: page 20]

9. Solder the power and ground connections to the header pins. Refer to Figure 28 to ensure power and ground are soldered to the correct header pins.
10. Solder the yellow jumper wires to the appropriate receptacle pins, and the 100 kΩ resistors to appropriate receptacle pins as shown in Figure 26:
Figure 24: Molex connector configurations | Figure 25: Breadboard orientation on hub

Figure 26: Finished soldered connections for breadboard hub, top and front view

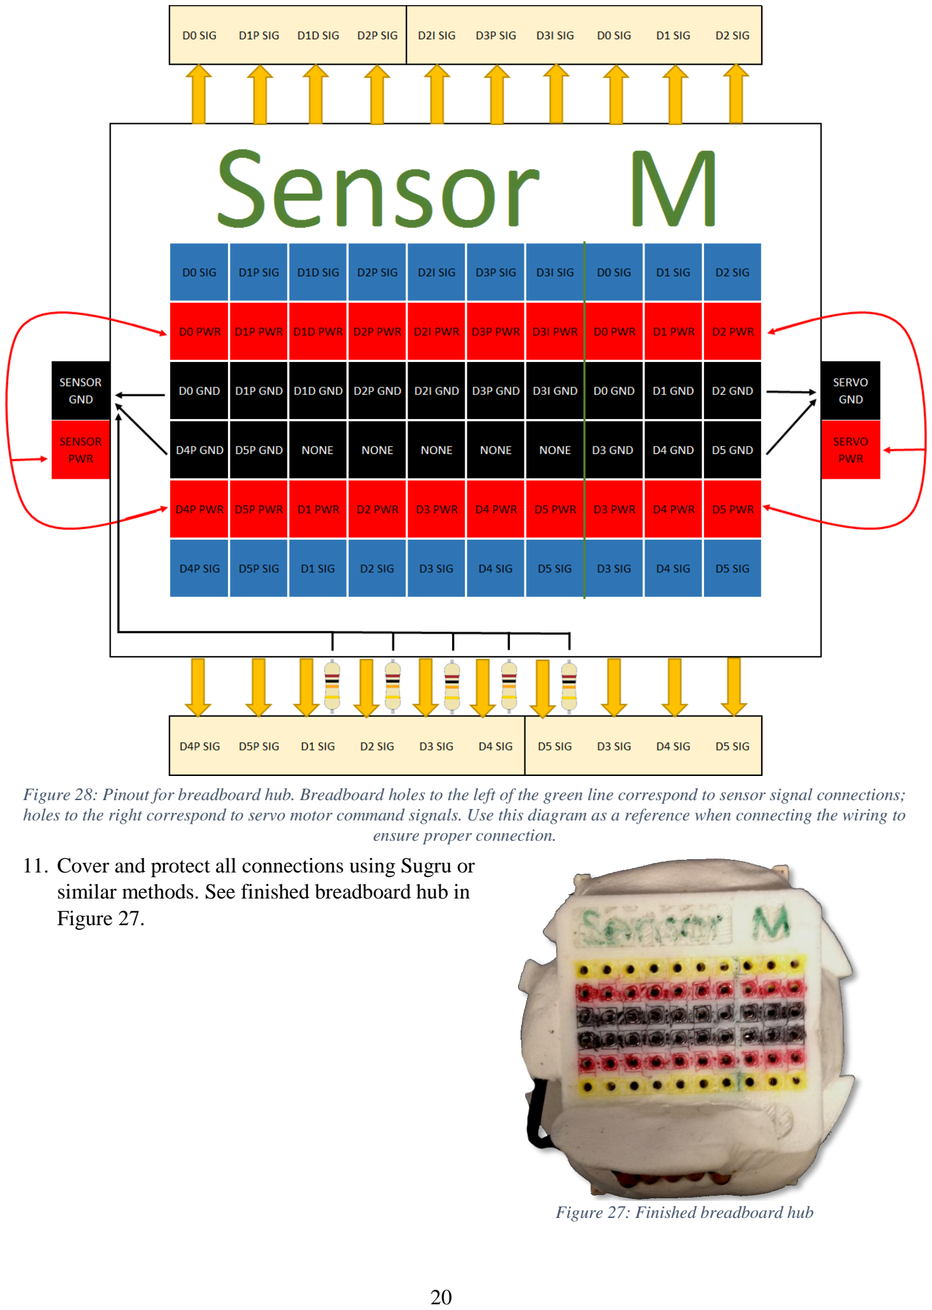
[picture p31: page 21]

11. Cover and protect all connections using Sugru or
similar methods. See finished breadboard hub in
Figure 27.

Figure 28: Pinout for breadboard hub. Breadboard holes to the left of the green line correspond to sensor signal connections; holes to the right correspond to servo motor command signals. Use this diagram as a reference when connecting the wiring to ensure proper connection.

Figure 27: Finished breadboard hub

## 10 Aluminum Servo Cover (0h 45m)

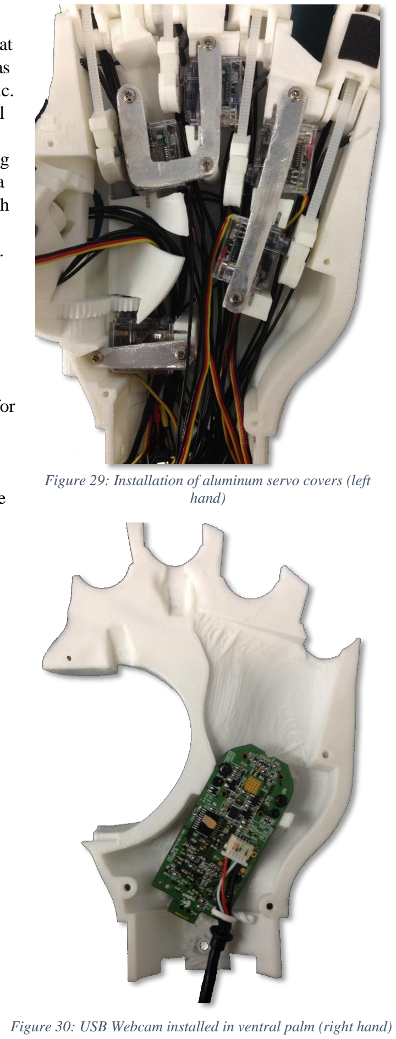
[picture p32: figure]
hand)

The servo covers are made of aluminum. They act as a heat sink and reduce the tendency to overheat the servos, and as well have less tendency to warp than the 3D printed plastic. They can be cut from the aluminum sheet given in the Bill of Materials, to the size and shape given in Appendix B: Servo Cover Template. Cut around the outside shape using tin snips, and file down to the exact shape and size using a flat metal file. Drill the holes using a 1/16” drill bit. Attach the servo covers using the coarse thread stainless steel phillips screws provided with the HS-35HD servo motors. Refer to Figure 29 for orientation of the servo covers for installation.

## 11 Ventral Palm Cover; USB Webcam (0h 20m)

The webcam used currently is a Logitech Quickcam Pro for Notebooks. Remove the PCB and lens from the camera housing, and mount it to the ventral palm using the extra small black screws that came with the HS-35HD servo motors. Figure 30 shows the USB webcam mounted to the ventral palm.

The USB cable from the camera will be routed out of the wrist cavity via the USB wire channel noted earlier in section 9 .

Mount the ventral palm to the front of the dorsal palm, being careful to ensure all wires are routed properly and there are no pinch points. The ventral palm is secured using four 12mm M2 screws.

Figure 30: USB Webcam installed in ventral palm (right hand)

Figure 29: Installation of aluminum servo covers (left

## 12 Palm Grips (1h 15m)

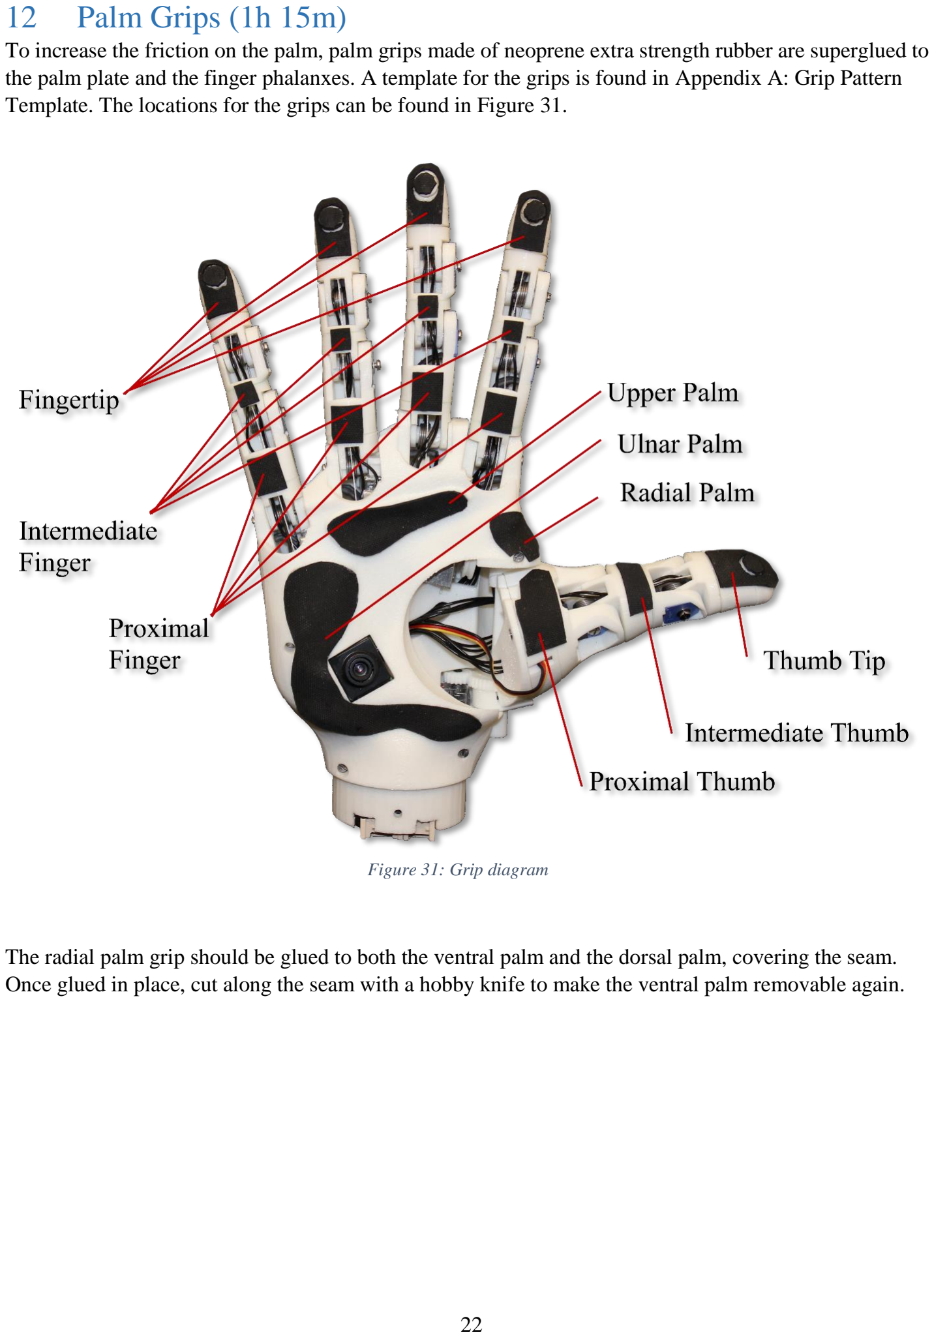
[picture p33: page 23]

To increase the friction on the palm, palm grips made of neoprene extra strength rubber are superglued to the palm plate and the finger phalanxes. A template for the grips is found in Appendix A: Grip Pattern Template. The locations for the grips can be found in Figure 31.

The radial palm grip should be glued to both the ventral palm and the dorsal palm, covering the seam. Once glued in place, cut along the seam with a hobby knife to make the ventral palm removable again.

Figure 31: Grip diagram

## 13 Wiring (1h 0m) 13.1 Testing

The following wiring diagram (Figure 32) is intended for use with the Arduino sketch Pot_to_Servo_Control.ino, for the purpose of testing an individual servo for tensioning, installation and testing finger movement.

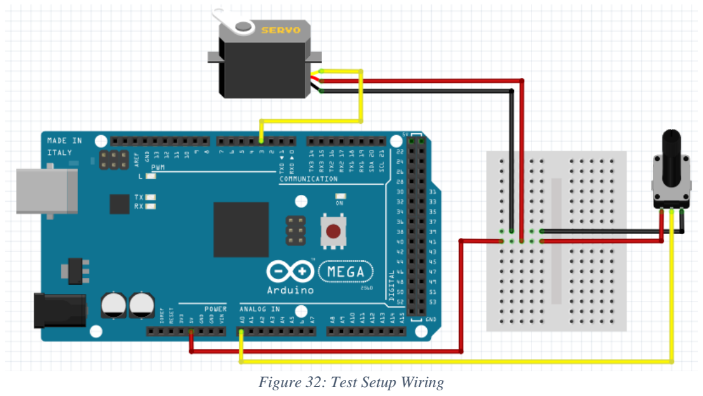
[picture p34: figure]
Figure 32: Test Setup Wiring
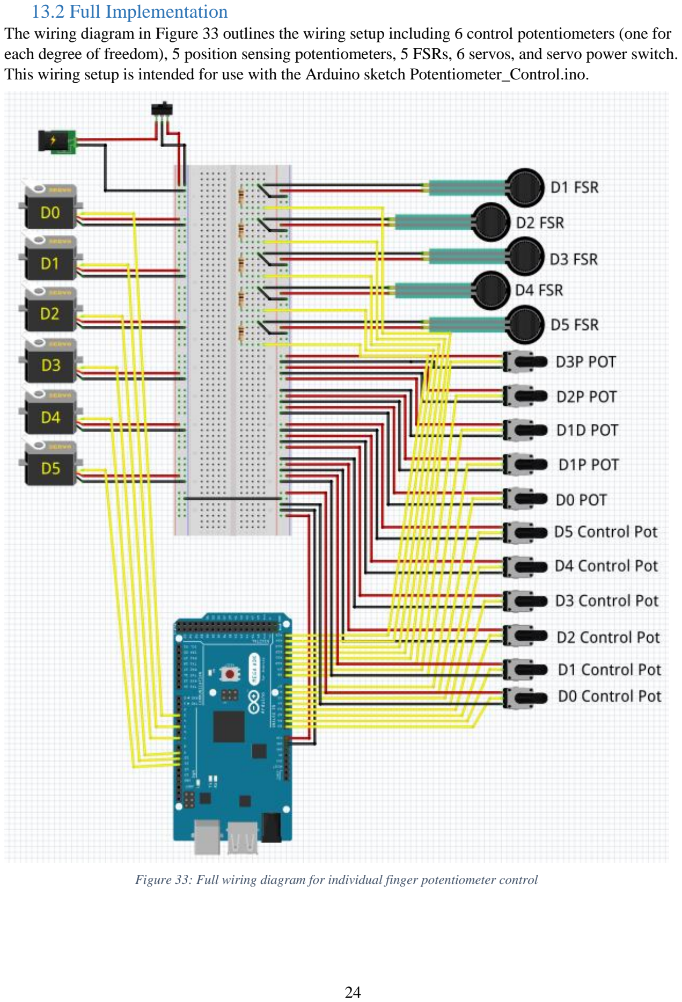
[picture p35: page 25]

### 13.2 Full Implementation

The wiring diagram in Figure 33 outlines the wiring setup including 6 control potentiometers (one for each degree of freedom), 5 position sensing potentiometers, 5 FSRs, 6 servos, and servo power switch. This wiring setup is intended for use with the Arduino sketch Potentiometer_Control.ino.

Figure 33: Full wiring diagram for individual finger potentiometer control

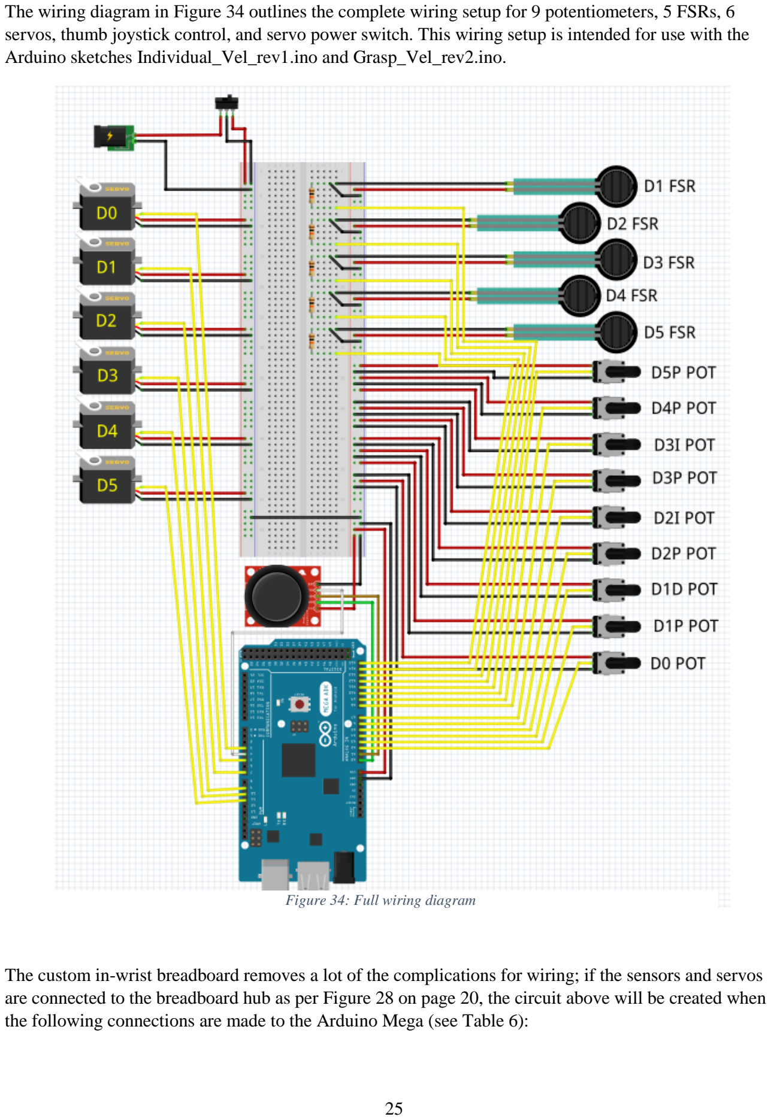
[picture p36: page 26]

The wiring diagram in Figure 34 outlines the complete wiring setup for 9 potentiometers, 5 FSRs, 6 servos, thumb joystick control, and servo power switch. This wiring setup is intended for use with the Arduino sketches Individual_Vel_rev1.ino and Grasp_Vel_rev2.ino.

The custom in-wrist breadboard removes a lot of the complications for wiring; if the sensors and servos are connected to the breadboard hub as per Figure 28 on page 20, the circuit above will be created when the following connections are made to the Arduino Mega (see Table 6):

Figure 34: Full wiring diagram

Table 6: Pin connections to Arduino Mega

Sensor | Pin on Arduino Mega
D0 Pot | A2
D1P Pot | A3
D1D Pot | A4
D2P Pot | A5
D2I Pot | A6
D3P Pot | A7
D3I Pot | A8
D4P Pot | A9
D5P Pot | A10
D1 FSR | A11
D2 FSR | A12
D3 FSR | A13
D4 FSR | A14
D5 FSR | A15
D0 Servo | Digital 3
D1 Servo | Digital 5
D2 Servo | Digital 6
D3 Servo | Digital 9
D4 Servo | Digital 10
D5 Servo | Digital 11

I

## 14 Appendix A: Grip Pattern Template

II

III

## 15 Appendix B: Servo Cover Template

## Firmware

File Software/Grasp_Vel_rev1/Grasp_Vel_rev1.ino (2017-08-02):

// Handi-Hand Individual Digit Velocity Controller
// Version 0.1
// Author: Michael (Rory) Dawson
//
// Objective: This sketch provides open loop control of each individual digit of the handi-hand by  mapping 
// the analog input from a thumb joystick to the angular velocity of an RC servomotor. The momentary switch on the 
// thumb joystick is used to switch control from one digit to another in a sequential fashion.
// 
// Definitions:
// d0: thumb rotation
// d1: thumb flex
// d2: index digit
// d3: middle digit
// d4: ring digit
// d5: baby digit
//
// grasp 0: standard precision pinch closed
// grasp 1: standard 3 jaw chuck closed
// grasp 2: column grip
// grasp 3: lateral grip
//
// References:
// arduino servo sweep example
// arduino thumb joystick example https://www.sparkfun.com/tutorials/272
// Structs: http://playground.arduino.cc/Code/Struct
// Sample compiler for initial testing: http://ideone.com/IPWy58

#include <Servo.h> 

// Create a servo object to control the servos
// int servo_number = 5;     // the number of servos in the hand - 1
Servo object[6]; // for some reason for pin 9 PWM to work this needs to be set to 6

// Define global array of structs to hold the parameters for each digit
struct digitParam {
  int pin;                 // the pwm pin that this digit will be assigned to
  int flex_limit;          // the position limit for flexion in microseconds
  int extend_limit;        // the position limit for extension in microseconds
  int min_vel;             // the minimum velocity
  int max_vel;             // the maximum velocity
  int pos;                 // the current target position
  int vel;                 // the current target velocity
} digit[6]; // need to make one more than the amount used because of some kind of bug in the compiler digit[5].flex_limit kept messing up the program (if i commented it out the servo would run fine)

// Assign joystick axis and buttons to pins on the arduino
// Also connect the joystick VCC to Arduino 5V, and joystick GND to Arduino GND.

const int VERT = 0; // analog
const int HORIZ = 1; // analog
const int SEL =  4; // digital
int prev_state = 1;
int servoID = 0;
int graspID = 0;
int chA_deadband = 50;  
int chA_neutral = 512;
int chB_deadband = 50; 
int chB_neutral = 512;

// This sketch outputs serial data at 9600 baud (open Serial Monitor to view).

void setup()
{
  // make the SEL line an input
  pinMode(SEL,INPUT_PULLUP);
  // turn on the pull-up resistor for the SEL line (see http://arduino.cc/en/Tutorial/DigitalPins)
  digitalWrite(SEL,HIGH);
  
  // Define thumb rotation parameters
  digit[0].pin = 3;              // the pwm pin that this digit will be assinged to
  digit[0].flex_limit = 2306;     // the position limit for flexion in microseconds
  digit[0].extend_limit = 1800;    // the position limit for extension in microseconds
  digit[0].min_vel = 0;           // the minimum velocity
  digit[0].max_vel = 60;         // the maximum velocity
  digit[0].pos = 1500;            // the current target position
  digit[0].vel = 0;               // the current target velocity
// digit[0] = {11 , 2500, 500, 0, 50, 0, 1};
  
  // Define thumb flexion parameters
  digit[1].pin = 5;              // the pwm pin that this digit will be assinged to
  digit[1].flex_limit = 1835;     // the position limit for flexion in microseconds
  digit[1].extend_limit = 1330;    // the position limit for extension in microseconds
  digit[1].min_vel = 0;           // the minimum velocity
  digit[1].max_vel = 60;         // the maximum velocity
  digit[1].pos = 1500;            // the current target position
  digit[1].vel = 0;               // the current target velocity

  // Define index finger flexion parameters
  digit[2].pin = 6;              // the pwm pin that this digit will be assinged to
  digit[2].flex_limit = 2353;     // the position limit for flexion in microseconds
  digit[2].extend_limit = 1000;    // the position limit for extension in microseconds
  digit[2].min_vel = 0;           // the minimum velocity
  digit[2].max_vel = 60;         // the maximum velocity
  digit[2].pos = 1500;            // the current target position
  digit[2].vel = 0;               // the current target velocity
  
  // Define middle finger flexion parameters
  digit[3].pin = 9;              // the pwm pin that this digit will be assinged to
  digit[3].flex_limit = 2198;     // the position limit for flexion in microseconds
  digit[3].extend_limit = 1016;    // the position limit for extension in microseconds
  digit[3].min_vel = 0;           // the minimum velocity
  digit[3].max_vel = 60;         // the maximum velocity
  digit[3].pos = 1500;            // the current target position
  digit[3].vel = 0;               // the current target velocity
  
  // Define ring finger flexion parameters
  digit[4].pin = 10;              // the pwm pin that this digit will be assinged to
  digit[4].flex_limit = 2109;     // the position limit for flexion in microseconds
  digit[4].extend_limit = 787;    // the position limit for extension in microseconds
  digit[4].min_vel = 0;           // the minimum velocity
  digit[4].max_vel = 60;         // the maximum velocity
  digit[4].pos = 1500;            // the current target position
  digit[4].vel = 0;               // the current target velocity
  
  // Define baby finger paramaters
  digit[5].pin = 11;              // the pwm pin that this digit will be assinged to
  digit[5].flex_limit = 1900;     // the position limit for flexion in microseconds     
  digit[5].extend_limit = 600;    // the position limit for extension in microseconds
  digit[5].min_vel = 0;           // the minimum velocity
  digit[5].max_vel = 60;         // the maximum velocity
  digit[5].pos = 1500;            // the current target position
  digit[5].vel = 0;               // the current target velocity

  // attaches the servo each pin to the corresponding servo object 
  object[0].attach(digit[0].pin);
  object[1].attach(digit[1].pin);
  object[2].attach(digit[2].pin);
  object[3].attach(digit[3].pin);
  object[4].attach(digit[4].pin);
  object[5].attach(digit[5].pin);
  
  // Set initial servo ID
  servoID = 1;
  
//  // set up serial port for output
//  Serial.begin(9600);
}

void loop() 
{
  int vertical, horizontal, select;
  
  // read all values from the joystick
  vertical = analogRead(VERT); // will be 0-1023
  horizontal = analogRead(HORIZ); // will be 0-1023
  select = digitalRead(SEL); // will be HIGH (1) if not pressed, and LOW (0) if pressed
  
  if (select == LOW && prev_state == HIGH)
  {
    graspID = graspID + 1;
     if (graspID > 3)
     {
     graspID = 0;
     }
  }
  // Update the switch state
  prev_state = select;
  
  if(vertical > chA_neutral + chA_deadband)
  {
    servoID = 1;
    digit[servoID].vel = map(vertical, chA_neutral, 1023, digit[servoID].min_vel, digit[servoID].max_vel);
    digit[servoID].pos = digit[servoID].pos - digit[servoID].vel;
    if(digit[servoID].pos <= digit[servoID].extend_limit)
      {
        digit[servoID].pos = digit[servoID].extend_limit;
      }
    
    servoID = 5;
    digit[servoID].vel = map(vertical, chA_neutral, 1023, digit[servoID].min_vel, digit[servoID].max_vel);
    digit[servoID].pos = digit[servoID].pos - digit[servoID].vel;
    if(digit[servoID].pos <= digit[servoID].extend_limit)
      {
        digit[servoID].pos = digit[servoID].extend_limit;
      }
    
    for(servoID = 2; servoID <= 4; servoID++)
    {
    digit[servoID].vel = map(vertical, chA_neutral, 1023, digit[servoID].min_vel, digit[servoID].max_vel);
    digit[servoID].pos = digit[servoID].pos + digit[servoID].vel;
    if(digit[servoID].pos >= digit[servoID].flex_limit)
      {
        digit[servoID].pos = digit[servoID].flex_limit;
      }
    }
    
    servoID = 0;
    digit[servoID].vel = map(vertical, chA_neutral, 1023, digit[servoID].min_vel, digit[servoID].max_vel);
    digit[servoID].pos = digit[servoID].pos + digit[servoID].vel;
    if(digit[servoID].pos >= digit[servoID].flex_limit)
      {
        digit[servoID].pos = digit[servoID].flex_limit;
      }
  
  }
  else if(vertical < chB_neutral - chB_deadband)
  {
    servoID = 1;
    digit[servoID].vel = map(vertical, chB_neutral, 0, digit[servoID].min_vel, digit[servoID].max_vel);
    digit[servoID].pos = digit[servoID].pos + digit[servoID].vel;
    if(digit[servoID].pos >= digit[servoID].flex_limit)
      {
        digit[servoID].pos = digit[servoID].flex_limit;
      }
   
    servoID = 5;
    digit[servoID].vel = map(vertical, chB_neutral, 0, digit[servoID].min_vel, digit[servoID].max_vel);
    digit[servoID].pos = digit[servoID].pos + digit[servoID].vel;
    if(digit[servoID].pos >= digit[servoID].flex_limit)
      {
        digit[servoID].pos = digit[servoID].flex_limit;
      }
   
    for(servoID = 2; servoID <= 4; servoID++)
    {
    digit[servoID].vel = map(vertical, chB_neutral, 0, digit[servoID].min_vel, digit[servoID].max_vel);
    digit[servoID].pos = digit[servoID].pos - digit[servoID].vel;
    if(digit[servoID].pos <= digit[servoID].extend_limit)
      {
        digit[servoID].pos = digit[servoID].extend_limit;
      }
    }
    
    servoID = 0;
    digit[servoID].vel = map(vertical, chB_neutral, 0, digit[servoID].min_vel, digit[servoID].max_vel);
    digit[servoID].pos = digit[servoID].pos - digit[servoID].vel;
    if(digit[servoID].pos <= digit[servoID].extend_limit)
      {
        digit[servoID].pos = digit[servoID].extend_limit;
      }
  }
  switch(graspID)
  {
    case 0:
      // GRIP 0 - Standard precision pinch closed
      digit[1].max_vel = 60;
      digit[0].pos = 1000;
      digit[1].flex_limit = 1305;
      digit[2].extend_limit = 657;
      digit[3].extend_limit = 600;
      digit[3].pos = digit[3].extend_limit + 100;
      digit[4].pos = digit[4].extend_limit + 100;
      digit[5].pos = digit[5].flex_limit - 100;
      break;
    
    case 1:
      // GRIP 1 - Standard 3 jaw chuck closed
      digit[1].max_vel = 60;
      digit[0].pos = 850;
      digit[1].flex_limit = 1938;
      digit[2].extend_limit = 1184;
      digit[3].extend_limit = 1321;
      digit[4].pos = digit[4].extend_limit + 100;
      digit[5].pos = digit[5].flex_limit - 100;
      break;
    
    case 2:
      // GRIP 2 - Column grip
      digit[1].max_vel = 11;
      digit[0].pos = 850;
      digit[1].flex_limit = 2150;
      digit[2].extend_limit = 748;
      digit[3].extend_limit = 1016;
      break;
      
    case 3:
      // GRIP 3 - Lateral grip
      digit[1].max_vel = 60;
      digit[1].flex_limit = 2150;
      digit[2].pos = digit[2].extend_limit + 100;
      digit[3].pos = digit[3].extend_limit + 100;
      digit[4].pos = digit[4].extend_limit + 100;
      digit[5].pos = digit[5].flex_limit - 100;
      break;
  }
  
//      object[servoID].writeMicroseconds(digit[servoID].pos);    // tell servo to go to position in variable 'pos'
    object[0].writeMicroseconds(digit[0].pos);    // tell servo to go to position in variable 'pos'
    object[1].writeMicroseconds(digit[1].pos);    // tell servo to go to position in variable 'pos' 
    object[2].writeMicroseconds(digit[2].pos);    // tell servo to go to position in variable 'pos' 
    object[3].writeMicroseconds(digit[3].pos);    // tell servo to go to position in variable 'pos' 
    object[4].writeMicroseconds(digit[4].pos);    // tell servo to go to position in variable 'pos' 
    object[5].writeMicroseconds(digit[5].pos);    // tell servo to go to position in variable 'pos'  
    delay(10);                       // waits 30ms for the servo to reach the position
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

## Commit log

2017-08-02 Initial release
    [Breadboard.STEP, Breadboard.STL, Connector Hub.STEP, Connector Hub.STL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]
2017-12-20 Added files for substitute components for adductible thumb option
    [MC - D L - Add A.step, MC - D L - Add B.step, MC - D L - Add Pivot.step, MC - P Main L - Add A.step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]
2017-12-21 Updated assembly manual to include adductible thumb option
2017-12-21 Deleted oversized assembly manual file for zipped file version instead
2018-02-05 Camera Update
    Changed Ventral Palm files and assembly manual to accomodate more inexpensive camera
    [Ventral Palm L.STEP, Ventral Palm L.STL, Ventral Palm R.STEP, Ventral Palm R.STL]
2018-02-13 Zip-tie Guide Addition
    Added zip-tie guides in IP - D and PP - D parts for all fingers to help with more complete range of motion.
    [IP - D L.STEP, IP - D L.STL, IP - D R.STEP, IP - D R.STL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]
2018-02-13 Manual Updates
    Updated Manual to include adductible thumb assembly, and addressed confusions brought forth by N. Olsen and M. Paskett of the University of Utah
2018-03-01 "Add.able Thumb" branding
    Included name "Add.able Thumb" in assembly manual. Also changed spelling
    from "adductible" to "adductable" accordingly...
2018-03-10 Dorsal Palm No Supports
    Added .STEP files for dorsal palm left and right hand versions without print supports.
2018-04-16 Minor updates to Add.able Thumb components to facilitate assembly
2018-04-16 Updated digit tip-locking mechanism
    [DP - D LockTH.STEP]
2018-04-20 Added Assembly STEP Files
    Included assembly STEP files for both right and left-handed versions.
2018-04-24 Modified Palm for Camera
    Camera in BOM is larger than expected; ventral palm corrected to suit.
    [Ventral Palm3.0 L.STEP, Ventral Palm3.0 L.STL, Ventral Palm3.0 R.STEP, Ventral Palm3.0 R.STL]
2018-04-24 Assembly STEP Files with new Ventral Palm
2018-04-25 Breadboard Allowance in Dorsal Palm
    Small cutouts at the wrist connection to allow for molex connectors
    [Dorsal Palm L.STL, Dorsal Palm R.STL]
2018-04-26 Added wrist connector for connection to Bento Arm
    [Wrist Connector.STEP, Wrist Connector.STL]
2019-03-23 Servo discontinuation notice
